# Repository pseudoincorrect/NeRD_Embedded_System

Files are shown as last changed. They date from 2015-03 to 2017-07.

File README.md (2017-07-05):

# Neural activity transmission device 

This repository describe the code of a neural activity transmission device embedded on a rodent.
The purpose of this system is to log the the electrical activity of a rat's neurones onto a computer.

## Global view of the acquisition system 

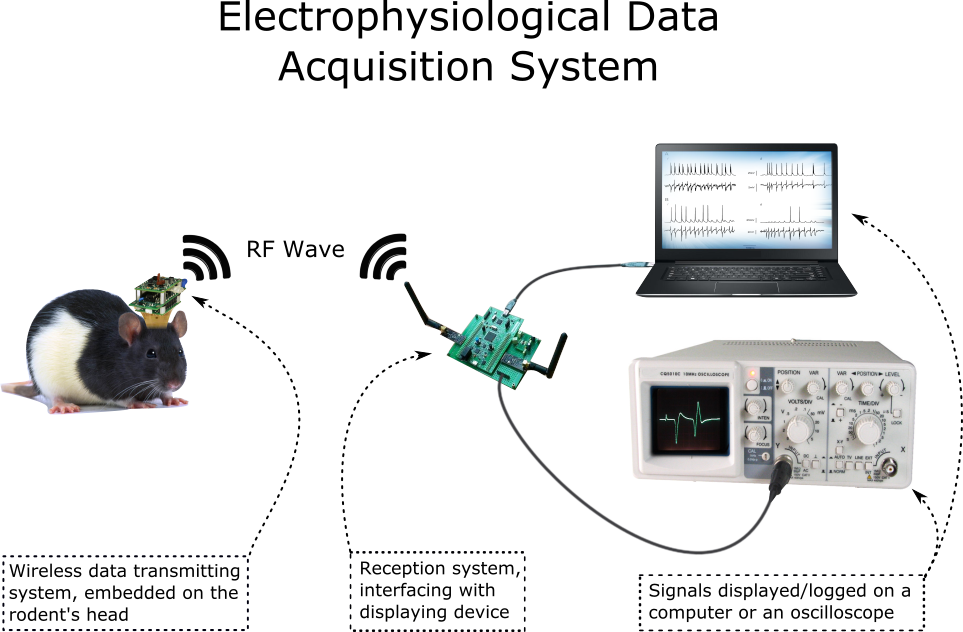
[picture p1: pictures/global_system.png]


[global_system]: https://github.com/pseudoincorrect/Electrophy_Embedded_System/blob/doxygen/pictures/global_system.png?raw=true "Global data acquisition system"

### This repository contain the code and the eagle file necessary to create a the transmitting system embedded on the rodent (see above)

### Features (Embedded Part)

* Omnetics adapter
* Transmit 4 channels of 16 bits at 20 kHz 
* Or 8 channels compressed (16 bits after decompression) at 20 kHz
* Consume 18 mA at 3.7 V at full transmission load
* Weight 7 grams 
* Volume : 2cm *2cm * 2cm 

### Features (Interface Part)

* USB audio protocol interface to display and log on PC
* 8 channels DAC to connect to an acquisition card
* USB as power supply

## Technical part

On this version, we use the Microcontroler [STM32f051C8T7](http://www.st.com/web/en/catalog/mmc/SC1169/SS1574/LN7/PF251889) to interface the Intantech [RHD2132](http://www.intantech.com/products_RHD2000.html) ADC device, and the Nordic Semiconductor [Nrf24l01+](http://www.nordicsemi.com/eng/Products/2.4GHz-RF/nRF24L01) RF transciever.

Eagle files and manual provided in this repertory

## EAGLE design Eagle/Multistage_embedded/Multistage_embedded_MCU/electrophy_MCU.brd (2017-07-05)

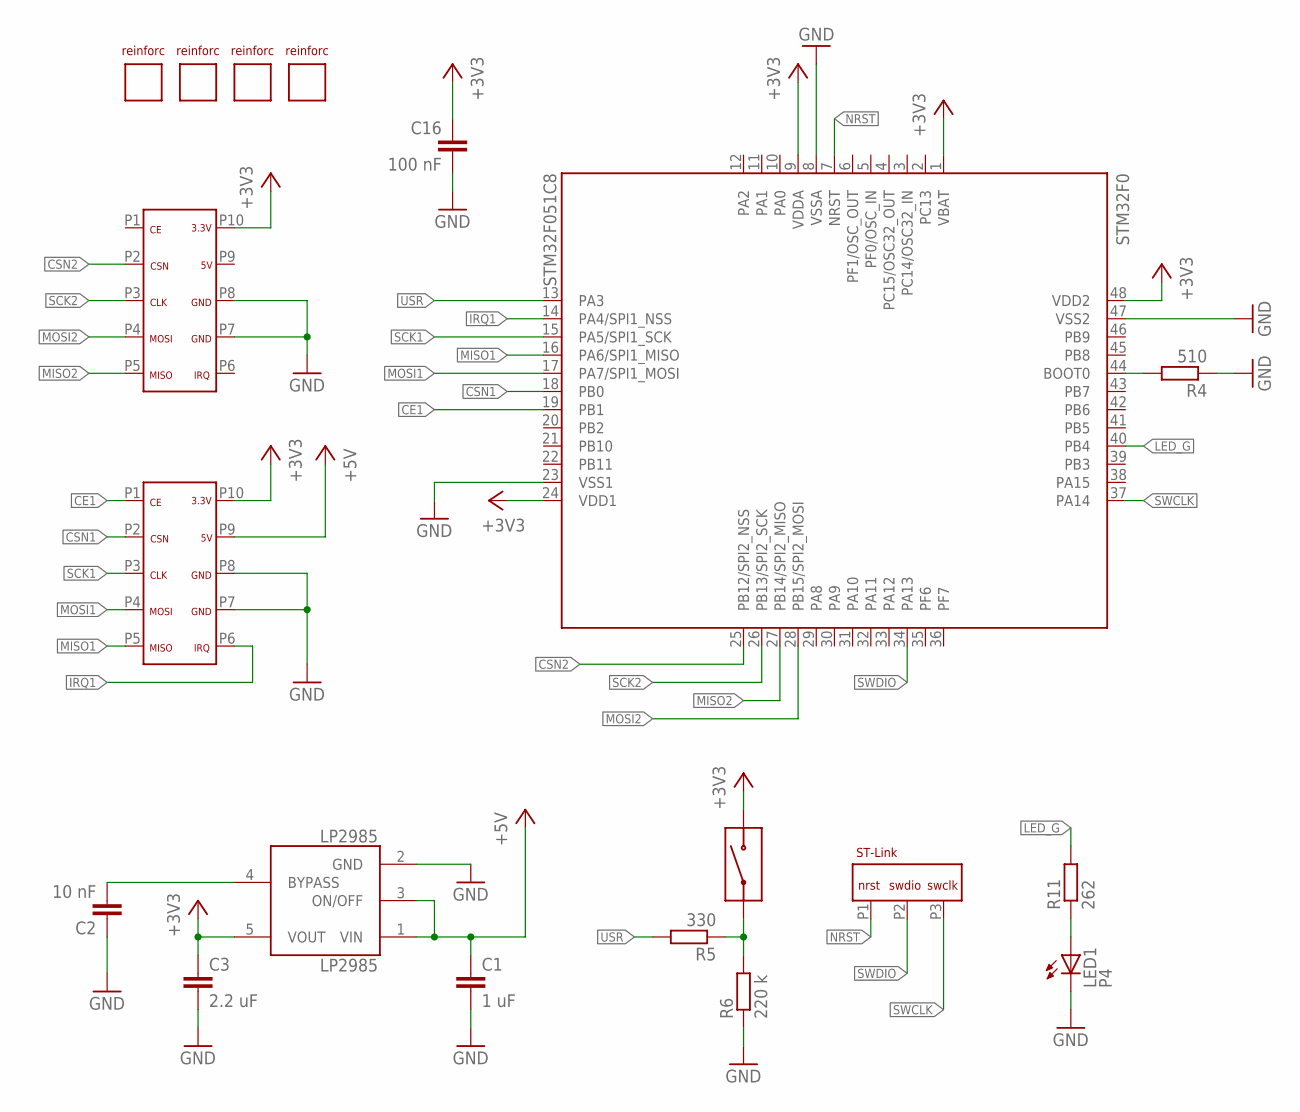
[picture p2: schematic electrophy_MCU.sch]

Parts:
C1: 1 uF; C0603
C2: 10 nF; C0603
C3: 2.2 uF; C0603
C16: 100 nF; C0603
LED1: P4; CHIPLED_0603
LP2985: LP2985AIM5-3.3; SOT25
R4: 510; R0603
R5: 330; R0603
R6: 220 k; R0603
R11: 262; R0603
STM32F0: STM32F051C8; LQFP48-7X7
U$1: DF12-10-FEMALE
U$2: PROGRAM_PIN
U$3: DF12-10-MALE
U$4: TACTILE_BUTTON_THROUGH
U$5, U$6, U$7, U$8: REINFORCEMENT

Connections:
+3V3: C3.1, C16.1, LP2985.5 (VOUT), STM32F0.1 (VBAT), STM32F0.9 (VDDA), STM32F0.24 (VDD1), STM32F0.48 (VDD2), U$1.P10, U$3.P10, U$4.P2 (2)
+5V: C1.1, LP2985.1 (VIN), LP2985.3 (ON/OFF), U$1.P9
BYPASS: C2.2, LP2985.4 (BYPASS)
CE1: STM32F0.19 (PB1), U$1.P1
CSN1: STM32F0.18 (PB0), U$1.P2
CSN2: STM32F0.25 (PB12/SPI2_NSS), U$3.P2
GND: C1.2, C2.1, C3.2, C16.2, LED1.C, LP2985.2 (GND), R4.1, R6.1, STM32F0.8 (VSSA), STM32F0.23 (VSS1), STM32F0.47 (VSS2), U$1.P7, U$1.P8, U$3.P7, U$3.P8
IRQ1: STM32F0.14 (PA4/SPI1_NSS), U$1.P6
LED_G: R11.2, STM32F0.40 (PB4)
MISO1: STM32F0.16 (PA6/SPI1_MISO), U$1.P5
MISO2: STM32F0.27 (PB14/SPI2_MISO), U$3.P5
MOSI1: STM32F0.17 (PA7/SPI1_MOSI), U$1.P4
MOSI2: STM32F0.28 (PB15/SPI2_MOSI), U$3.P4
unnamed: R5.1, R6.2, U$4.P1 (1)
unnamed: R4.2, STM32F0.44 (BOOT0)
unnamed: LED1.A, R11.1
NRST: STM32F0.7 (NRST), U$2.P1
SCK1: STM32F0.15 (PA5/SPI1_SCK), U$1.P3
SCK2: STM32F0.26 (PB13/SPI2_SCK), U$3.P3
SWCLK: STM32F0.37 (PA14), U$2.P3
SWDIO: STM32F0.34 (PA13), U$2.P2
USR: R5.2, STM32F0.13 (PA3)

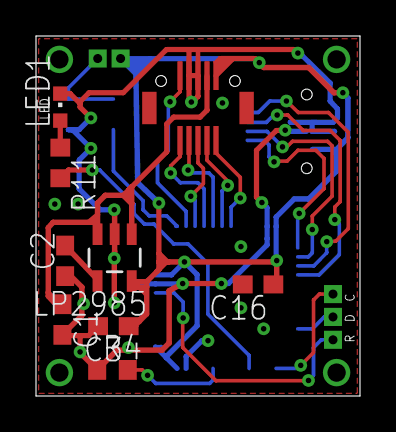
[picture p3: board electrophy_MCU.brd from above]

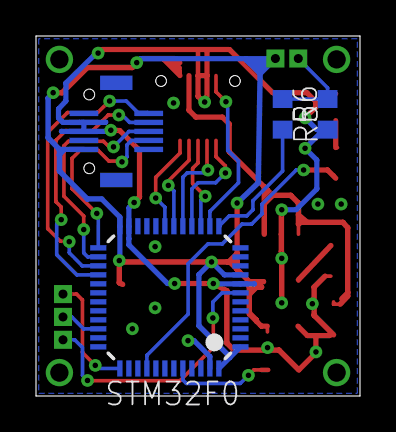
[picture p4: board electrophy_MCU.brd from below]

Board: 2 copper layers, 18.0 x 20.0 mm, 19 parts (5 on the bottom side), 22 nets.

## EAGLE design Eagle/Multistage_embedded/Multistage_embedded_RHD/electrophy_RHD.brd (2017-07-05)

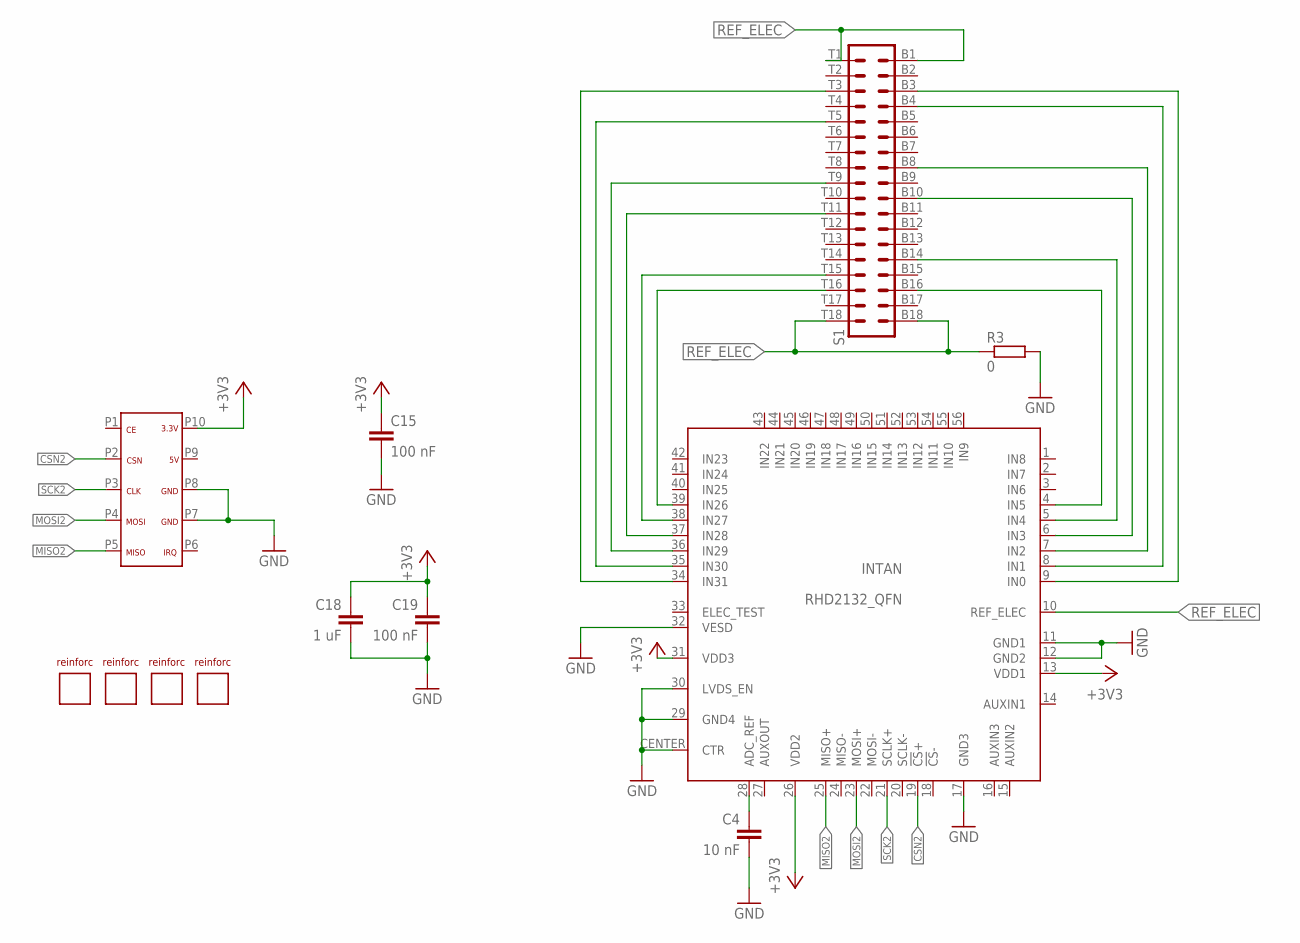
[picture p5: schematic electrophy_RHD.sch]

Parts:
C4: 10 nF; C0603
C15, C19: 100 nF; C0603
C18: 1 uF; C0603
INTAN: RHD2132_QFN; QFN56_8_X_8_LARGE
R3: 0; R0603
S1: OMNETICS_A79027
U$1: DF12-10-FEMALE
U$2, U$3, U$4, U$5: REINFORCEMENT

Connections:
+3V3: C15.1, C18.1, C19.1, INTAN.13 (VDD1), INTAN.26 (VDD2), INTAN.31 (VDD3), U$1.P10
CSN2: INTAN.19 (!CS!+), U$1.P2
GND: C4.2, C15.2, C18.2, C19.2, INTAN.11 (GND1), INTAN.12 (GND2), INTAN.17 (GND3), INTAN.29 (GND4), INTAN.30 (LVDS_EN), INTAN.32 (VESD), INTAN.CENTER (CTR), R3.2, U$1.P7, U$1.P8
MISO2: INTAN.25 (MISO+), U$1.P5
MOSI2: INTAN.23 (MOSI+), U$1.P4
unnamed: INTAN.4 (IN5), S1.B16
unnamed: INTAN.34 (IN31), S1.T3
unnamed: INTAN.35 (IN30), S1.T5
unnamed: INTAN.38 (IN27), S1.T15
unnamed: INTAN.39 (IN26), S1.T16
unnamed: C4.1, INTAN.28 (ADC_REF)
unnamed: INTAN.8 (IN1), S1.B4
unnamed: INTAN.9 (IN0), S1.B3
unnamed: INTAN.5 (IN4), S1.B14
unnamed: INTAN.7 (IN2), S1.B8
unnamed: INTAN.6 (IN3), S1.B10
unnamed: INTAN.36 (IN29), S1.T9
unnamed: INTAN.37 (IN28), S1.T11
REF_ELEC: INTAN.10 (REF_ELEC), R3.1, S1.B1, S1.B18, S1.T1, S1.T18
SCK2: INTAN.21 (SCLK+), U$1.P3

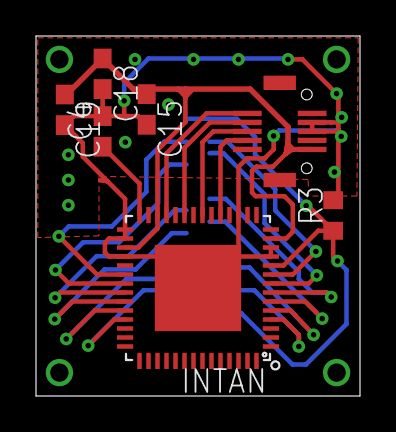
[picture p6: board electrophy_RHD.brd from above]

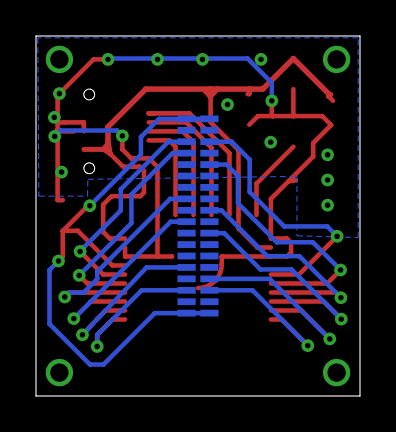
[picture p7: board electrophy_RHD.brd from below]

Board: 2 copper layers, 18.0 x 20.0 mm, 12 parts (2 on the bottom side), 20 nets.

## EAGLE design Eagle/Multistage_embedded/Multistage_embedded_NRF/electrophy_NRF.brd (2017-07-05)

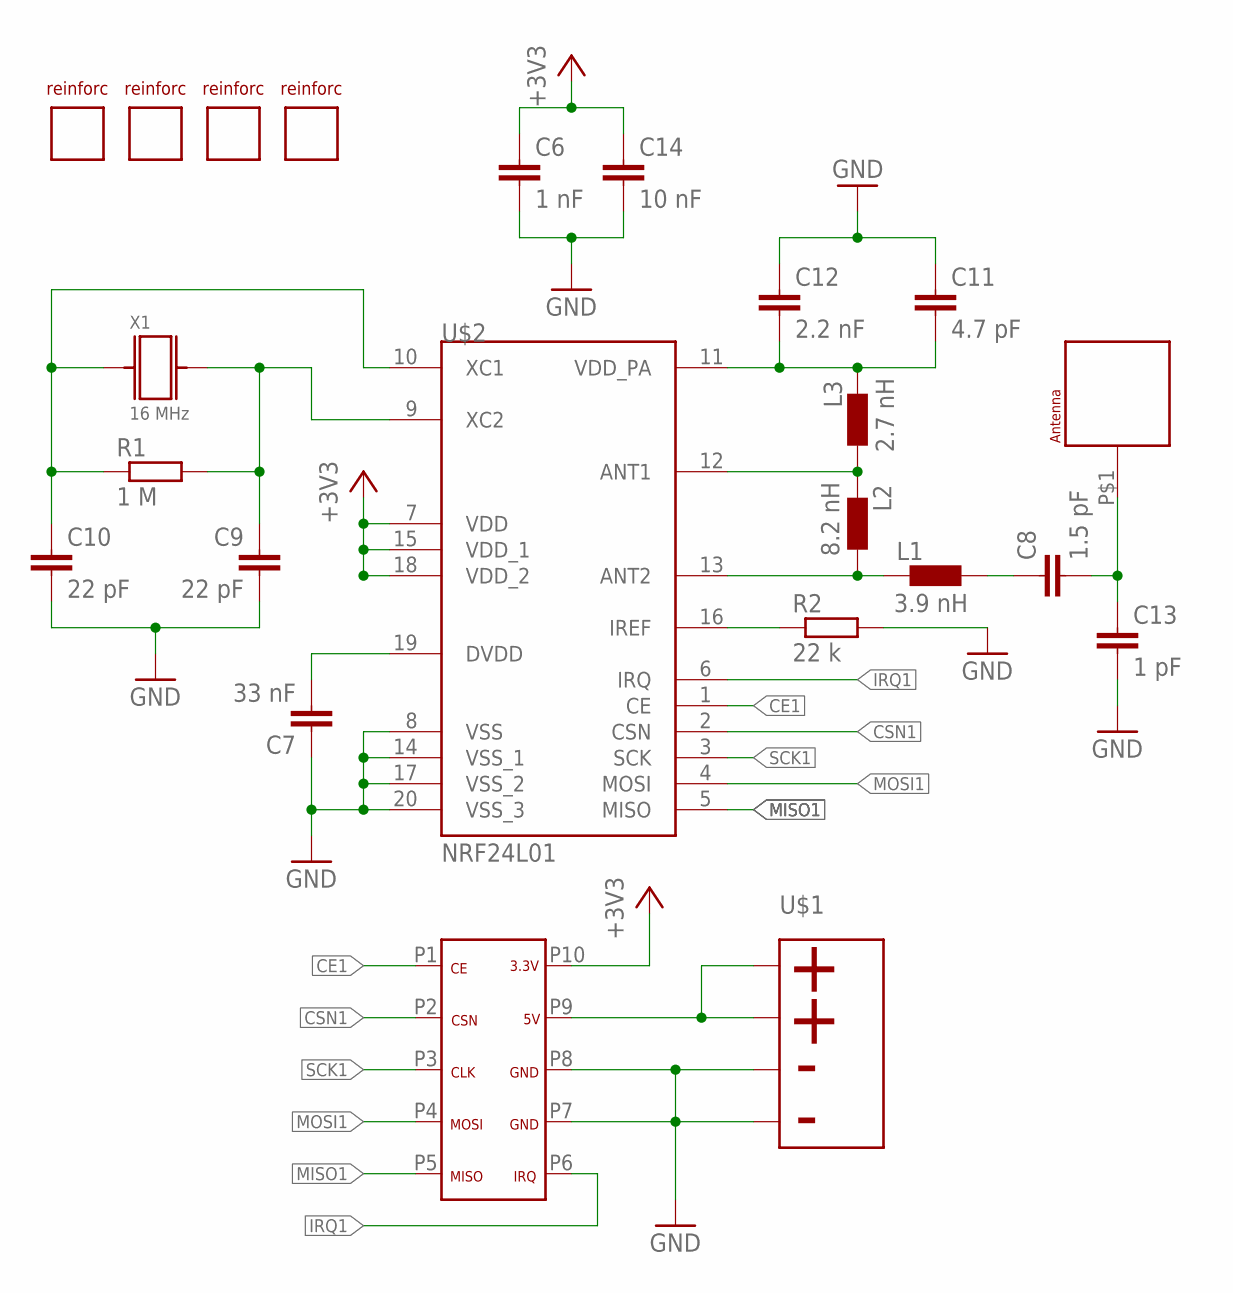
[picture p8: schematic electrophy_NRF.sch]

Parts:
C6: 1 nF; C0603
C7: 33 nF; C0603
C8: 1.5 pF; C0603
C9, C10: 22 pF; C0603
C11: 4.7 pF; C0603
C12: 2.2 nF; C0603
C13: 1 pF; C0603
C14: 10 nF; C0603
L1: 3.9 nH; C0603
L2: 8.2 nH; C0603
L3: 2.7 nH; C0603
R1: 1 M; R0603
R2: 22 k; R0603
U$1: BAT_HOLDER
U$2: NRF24L01; QFN20
U$3: WURTH_ANTENNA
U$4: DF12-10-MALE
U$5, U$6, U$7, U$8: REINFORCEMENT
X1: 16 MHz; NRF_XTAL

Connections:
+3V3: C6.1, C14.1, U$2.7 (VDD), U$2.15 (VDD_1), U$2.18 (VDD_2), U$4.P10
CE1: U$2.1 (CE), U$4.P1
CSN1: U$2.2 (CSN), U$4.P2
GND: C6.2, C7.1, C9.2, C10.2, C11.1, C12.1, C13.2, C14.2, R2.2, U$1.PMOINS, U$1.PMOINSBIS, U$2.8 (VSS), U$2.14 (VSS_1), U$2.17 (VSS_2), U$2.20 (VSS_3), U$4.P7, U$4.P8
IRQ1: U$2.6 (IRQ), U$4.P6
MISO1: U$2.5 (MISO), U$4.P5
MOSI1: U$2.4 (MOSI), U$4.P4
unnamed: C7.2, U$2.19 (DVDD)
unnamed: C11.2, C12.2, L3.2, U$2.11 (VDD_PA)
unnamed: R2.1, U$2.16 (IREF)
unnamed: L1.2, L2.1, U$2.13 (ANT2)
unnamed: C9.1, R1.2, U$2.9 (XC2), X1.P$1 (1)
unnamed: L2.2, L3.1, U$2.12 (ANT1)
unnamed: C8.2, C13.1, U$3.P$1
unnamed: C8.1, L1.1
unnamed: C10.1, R1.1, U$2.10 (XC1), X1.P$2 (2)
PPLUS: U$1.PPLUS, U$1.PPLUSBIS, U$4.P9
SCK1: U$2.3 (SCK), U$4.P3

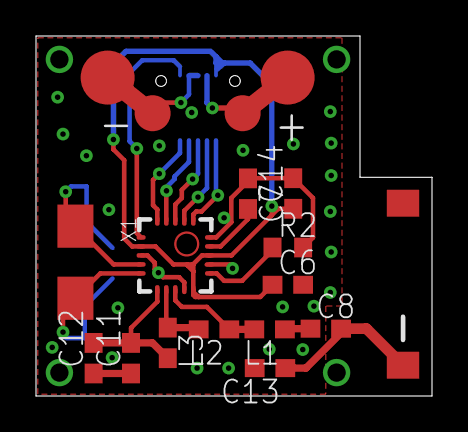
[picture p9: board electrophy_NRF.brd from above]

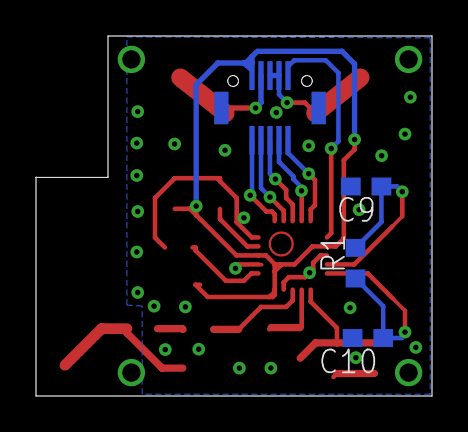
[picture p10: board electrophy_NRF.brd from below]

Board: 2 copper layers, 22.0 x 20.0 mm, 23 parts (4 on the bottom side), 18 nets.

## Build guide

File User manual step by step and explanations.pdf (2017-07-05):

# User manual step by step and explanations

This file will reunite all the instructions to build the hardware part of the rat embedded system and of the interfacing system. We will describe as well how to download the codes in them.

Quick description of the system

The embedded emitting system connected to the implant of the rat, will digitalize the neural signals with an analog to digital converter, compress data, before sending them wirelessly to the second system. This latter, after reception, will decompress data, converted them into USB packets and finally transmit them to the computer for display and recording.

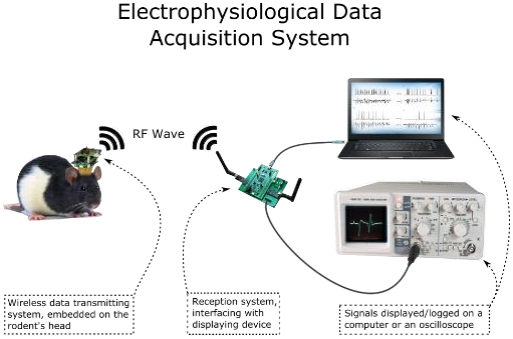
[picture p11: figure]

Summary

I) Building the neural recording System
- How to create, the rat head stage PCB
- Display it on Eagle
- Order it from a PCB creating company on internet
- Solder the components
- How to create the Interfacing system
- Solder components
- How to program the system
- Setup of Keil (software)
- Setup of ST link V2
- Program the two microcontrollers
- How to test the system

II) Explanation about the System • General explanation about the system • Explanations about the Code

Glossary:

MCU: microcontroller
RHD: Rhd2132 the analog to digital module that will convert the neural signal of the rat
NRF: | Nrf24L01+ the transceiver module used to communicate wirelessly
PCB: | Printed circuit board
Embedded system: | the system that will be carried by the rat on its head
Interfacing system: | the system that will do the interface between the embedded system and the
computer

# Building the neural recording System

# How to create, the rat head stage PCB

## Display on Eagle

First, we have to download Eagle, a software from Cadsoft from their website. The free version, is enough. We take the last version, corresponding with our OS (windows 7, 64 bits in our case)

http://www.cadsoftusa.com/download-eagle

Now, it’s time to install it.

Now download the file: [lien]
Since the Embedded system is composed of 3 sub-systems, we have 3 different eagle files/folders. We open one of the, for instance [blab la bla.egl].

We can follow this [link tutorial] tutorial to increase our understanding and be able to navigate between files. As we open it, three windows will be displayed one for the project manager, one for the schematics of the circuit and one for the actual representation and design of the circuit.

Order PCB’s

Since we only want to order printed circuit and not design it, we won’t say more about eagle. Many tutorial are available on internet.

To order the printed circuits, we need to pick on PCB manufacturer available on internet and which accept PCB layout file under eagle file format. For the following of this tutorial, we will use PCB-Pool printed circuit manufacturer: [pcb pool]

Again, since the embedded system is composed of 3 PCB, we have to do 3 orders. On the PCB pol website (the English version), we go to “Order” → “PCB’s”. Then we fill the formulary. To reduce the price you can unselect some option, but we advise to use the option as shown below. Also you can select another manufacturer to reduce the costs. The solution we give is just a working example.

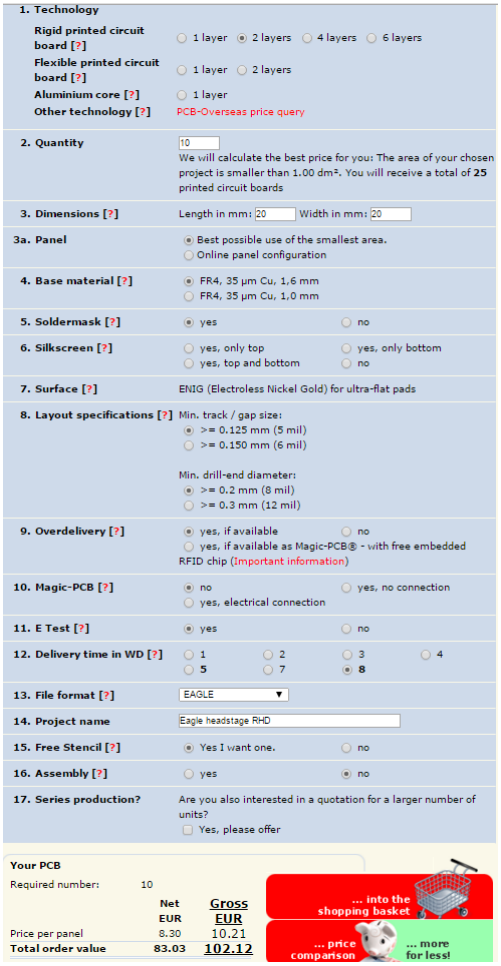
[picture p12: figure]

Components list
Be sure to order every components needed, which are listed [here] in their correct package.

## Soldering

Soldering is the most delicate part of building the system. Many technics are usable such as using a soldering iron, a hot air soldering station, or a reflow oven. In our case we soldered every component except the RHD2132 and the NRF24L01+ whit a soldering iron. For the later component, we used a hot air soldering station. About soldering, many tutorials exists as well (youtube.com).
The advices we can give are the following:
- Use a microscope or a good lens
- Set first the components intended to be soldered by hot air
- Then set first the most complicated to solder components (microcontroller, Led, connectors)

How to create the interface system

The interface system is centered on a STMicroelectronics development board, the STM32F411 development board:

http://www.st.com/web/catalog/tools/FM116/SC959/SS1532/LN1848/PF260946

Follow this list of components to create the interfacing system

[List]

And solder them following that schematic.

[Schematic]
There is no particular difficulties for soldering these components.

# How to program the system

This section will speak about how to set up the system. We won’t approach the understanding of the code and the utilization of Keil the development tool used to develop the code and debug the system. We will see how to compile the code and program both MCU’s.

First we need to install the last version of Keil:
- Let’s go to: http://www.keil.com/
- Then: “product download” → “MDK-ARM”
- Then: we complete the formulary and download the software compatible with our Operating system, in our case, windows 7, and 64 bits.
- Then we install it.

- Doing this quick tutorial will help you a lot about working with Keil and the microcontroller we want to program:
http://www.keil.com/appnotes/files/apnt_261.pdf

Now it’s time to download the code from internet, open it in Keil and compile it.
Since we have two systems: the rat embedded one and the interfacing one, there is two projects under Keil. One project to create the code for each microcontroller. We want to compile the code of each project one at time, compile it, and download it to the corresponding microcontroller.

For that:
We go to: https://github.com/pseudoincorrect/Electrophy_Base_System
And click on “download zip”.

Then we go to: https://github.com/pseudoincorrect/Electrophy_Embedded_System And click on “download zip” as well.

## Keil project setting up

On each folder (after unzipping), we navigate to: Base_System or Embedded_System → Projects → MDK-ARM → and open the .uvprojx file (either Embedded_System.uvprojx or Base_System.uvprojx)

This will open the corresponding Keil project. Since we presume it’s the first we open Keil, some packages are needed to be added in order to compile properly and to download the code to the MCU.

After open, Keil will ask to choose either:
“Migrate to Device Pack” or “Install Legacy Support”, we choose the first one, “Migrate to Device Pack”.

Then depending which project we opened we will follow the appropriate one

## For the INTERFACING SYSTEM

If the “pack installer” is not opened, we open it by clicking on “Project” →“Manage” →“Pack installer”

Base_System.uvprojx

Go to device TAB
Go to:
“STMincroelectronics” →
“STM32F4 Series” | →
“STM32F411VE” | →
Click on “STM32F411VETx”

Go to Packs TAB
Install:
“Keil::STM32F4xx_DFP”

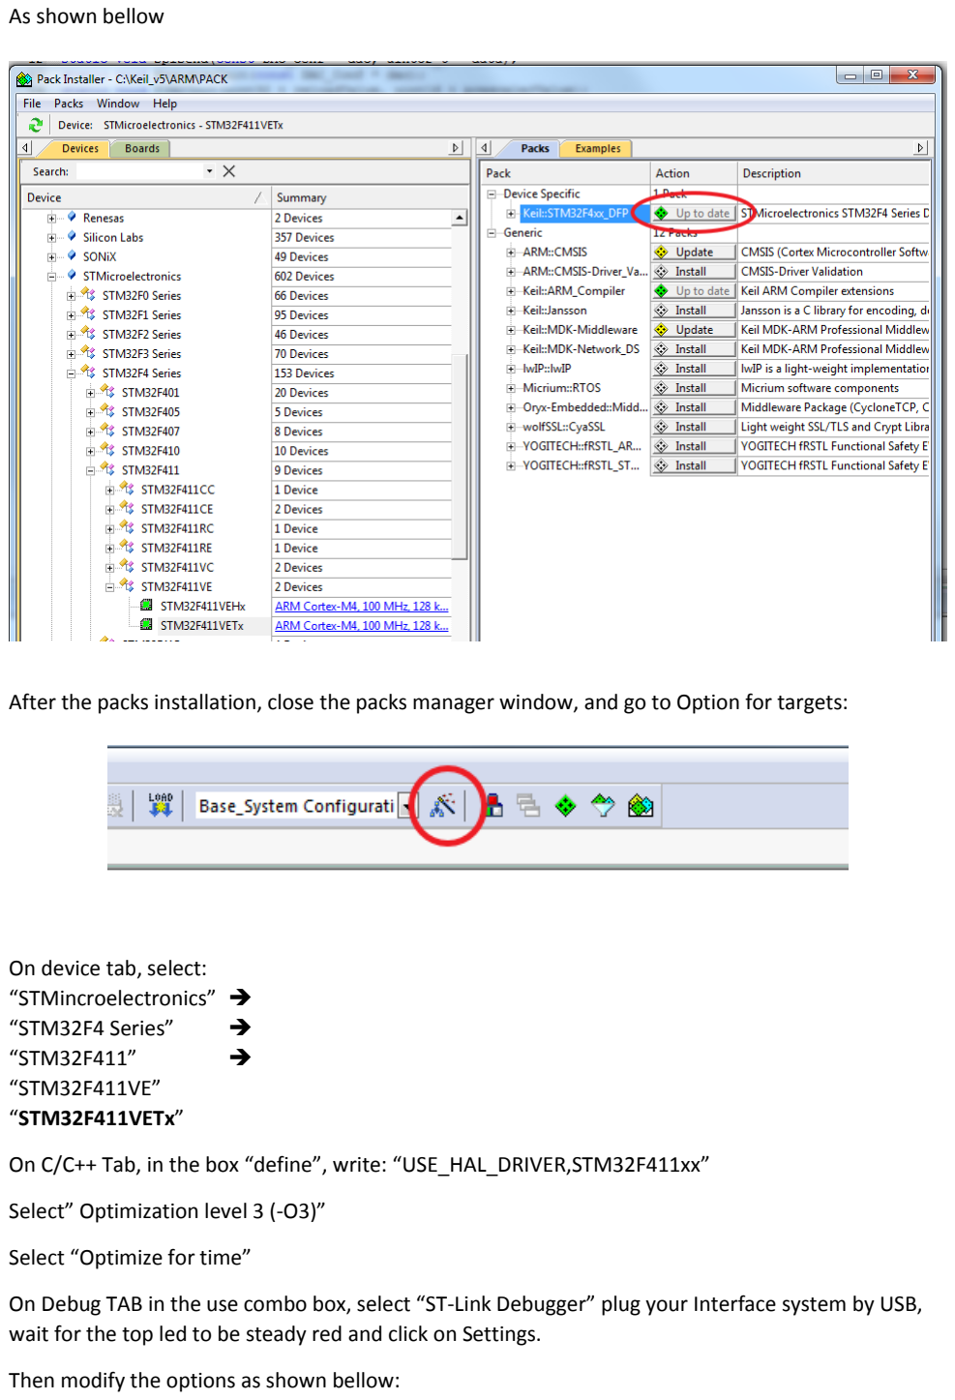
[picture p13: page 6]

As shown bellow

After the packs installation, close the packs manager window, and go to Option for targets:

On device tab, select:
“STMincroelectronics” →
“STM32F4 Series” | →
“STM32F411” | →
“STM32F411VE”
“STM32F411VETx”

On C/C++ Tab, in the box “define”, write: “USE_HAL_DRIVER,STM32F411xx”

Select” Optimization level 3 (-O3)”

Select “Optimize for time”

On Debug TAB in the use combo box, select “ST-Link Debugger” plug your Interface system by USB, wait for the top led to be steady red and click on Settings.

Then modify the options as shown bellow:

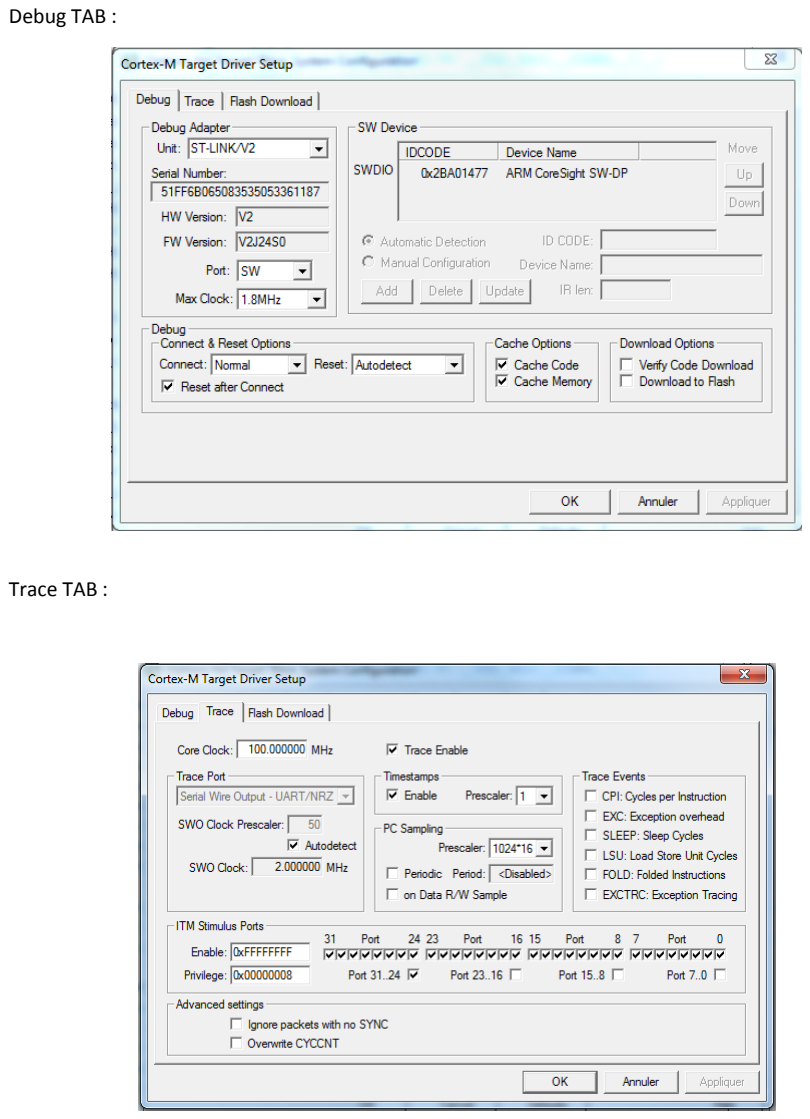
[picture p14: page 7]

Debug TAB :

Trace TAB :

Flash Download TAB:

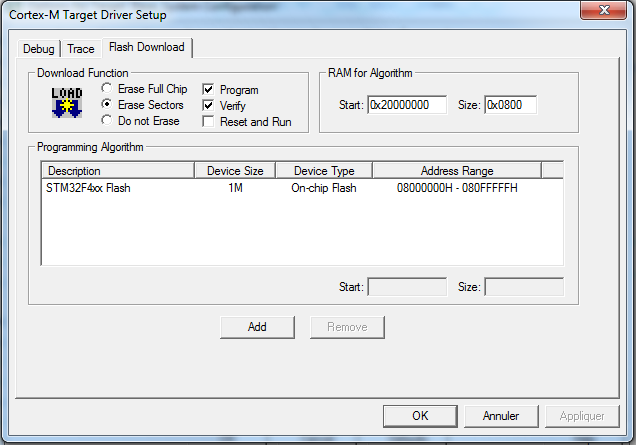
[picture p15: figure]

If there is nothing in Program Algorithm, select the one above “STM324xx Flash” by clicking on “Add”.

If this algorithm isn’t proposed, it’s because the proper pack isn’t installed, in pack manager, as saw above.

## For the EMBEDDED SYSTEM

If the “pack installer” is not opened, we open it by clicking on “Project” →“Manage” →“Pack installer”

Base_System.uvprojx

Go to device TAB
Go to:
“STMincroelectronics” →
“STM32F0 Series” | →
“STM32F051” | →
Click on “STM32F051C8”

Go to Packs TAB
Install:
“Keil::STM32F0xx_DFP”

As shown bellow

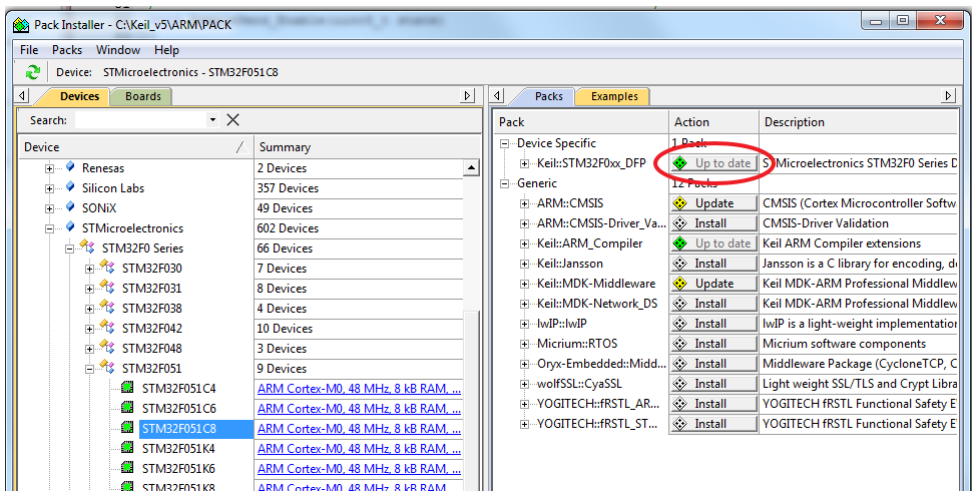
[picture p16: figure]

After the packs installation, close the packs manager window, and go to Option for targets:

On device tab, select:
“STMincroelectronics” →
“STM32F0 Series” | →
“STM32F051” | →
“STM32F051C8”

On C/C++ Tab, in the box “define”, write: “USE_HAL_DRIVER,STM32F051x8”

Select” Optimization level 3 (-O3)”

Select “Optimize for time”

On Debug TAB in the use combo box, select “ST-Link Debugger” plug your Interface system by USB, wait for the top led to be steady red and click on Settings.

Then modify the options as shown below

Debug TAB:

Trace TAB:

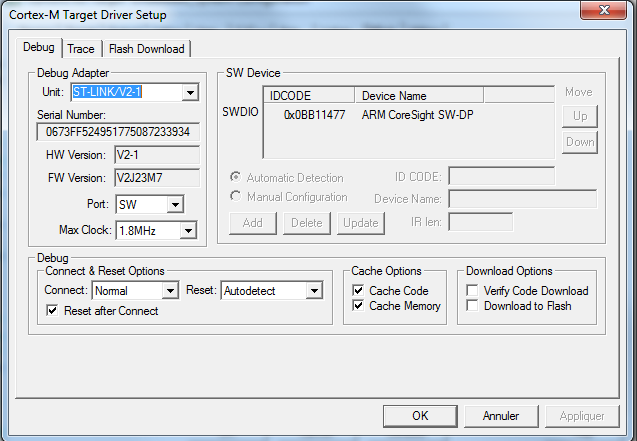
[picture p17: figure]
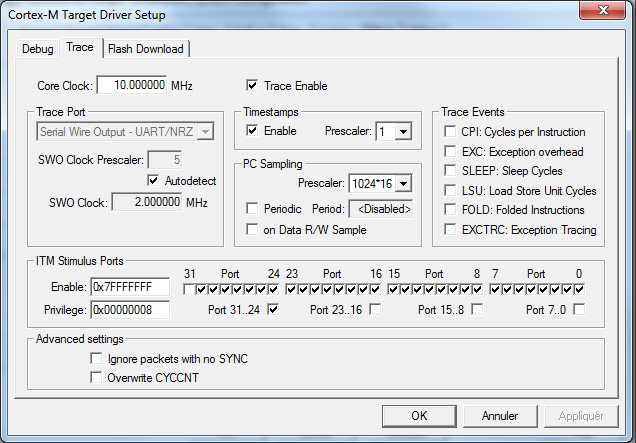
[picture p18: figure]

Flash Download TAB:

If there is nothing in Program Algorithm, select the one above “STM324xx Flash” by clicking on “Add”.

If this algorithm isn’t proposed, it’s because the proper pack isn’t installed, in pack manager, as saw above.

## Compilation of the Code and download to the microcontroller

To compile the code click on the Rebuild icon

If the compilation succeeded, we will get this message in the build Output console:

Otherwise, if we get error, a “Target not created” message will be displayed in the console. Which in that case a debugging is needed.

Now that the compilation was successful, we check that the target (the microcontroller) is linked and detected by the software by clicking on “option for target” → “Debug” tab → “Settings” button. And see if there is “ARM CoreSight SW-DP” in the SW Device block.

Then close the windows and click on “Download”

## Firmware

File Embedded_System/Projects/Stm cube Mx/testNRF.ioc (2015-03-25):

#MicroXplorer Configuration settings - do not modify
#Wed Jan 28 12:24:36 CET 2015
Dma.Request0=SPI1_TX
Dma.RequestsNb=1
Dma.SPI1_TX.0.Direction=DMA_MEMORY_TO_PERIPH
Dma.SPI1_TX.0.Instance=DMA1_Channel3
Dma.SPI1_TX.0.MemDataAlignment=DMA_MDATAALIGN_BYTE
Dma.SPI1_TX.0.MemInc=DMA_MINC_ENABLE
Dma.SPI1_TX.0.Mode=DMA_NORMAL
Dma.SPI1_TX.0.PeriphDataAlignment=DMA_PDATAALIGN_BYTE
Dma.SPI1_TX.0.PeriphInc=DMA_PINC_DISABLE
Dma.SPI1_TX.0.Priority=DMA_PRIORITY_LOW
Dma.SPI1_TX.0.RequestParameters=Instance,Direction,PeriphInc,MemInc,PeriphDataAlignment,MemDataAlignment,Mode,Priority
File.Version=4
KeepUserPlacement=false
Mcu.Family=STM32F0
Mcu.IP0=DMA
Mcu.IP1=NVIC
Mcu.IP2=RCC
Mcu.IP3=SPI1
Mcu.IP4=SPI2
Mcu.IPNb=5
Mcu.Name=STM32F051C8Tx
Mcu.Package=LQFP48
Mcu.Pin0=PA4
Mcu.Pin1=PA5
Mcu.Pin10=PA15
Mcu.Pin11=PB4
Mcu.Pin12=PB5
Mcu.Pin2=PA6
Mcu.Pin3=PA7
Mcu.Pin4=PB0
Mcu.Pin5=PB1
Mcu.Pin6=PB13
Mcu.Pin7=PB14
Mcu.Pin8=PB15
Mcu.Pin9=PF7
Mcu.PinsNb=13
Mcu.UserName=STM32F051C8Tx
MxCube.Version=4.5.0
NVIC.DMA1_Channel2_3_IRQn=true\:0\:0\:false
NVIC.SPI2_IRQn=true\:0\:0\:false
NVIC.SysTick_IRQn=true\:0\:0\:false
PA15.Locked=true
PA15.Signal=GPIO_Input
PA4.GPIOParameters=GPIO_PuPd,GPIO_Label,GPIO_Mode
PA4.GPIO_Label=Spi1Nss
PA4.GPIO_Mode=GPIO_MODE_INPUT
PA4.GPIO_PuPd=GPIO_NOPULL
PA4.Locked=true
PA4.Signal=GPIO_Input
PA5.Mode=Full_Duplex_Master
PA5.Signal=SPI1_SCK
PA6.Mode=Full_Duplex_Master
PA6.Signal=SPI1_MISO
PA7.Mode=Full_Duplex_Master
PA7.Signal=SPI1_MOSI
PB0.Locked=true
PB0.Signal=GPIO_Output
PB1.Locked=true
PB1.Signal=GPIO_Output
PB13.Mode=Full_Duplex_Master
PB13.Signal=SPI2_SCK
PB14.Mode=Full_Duplex_Master
PB14.Signal=SPI2_MISO
PB15.Mode=Full_Duplex_Master
PB15.Signal=SPI2_MOSI
PB4.Locked=true
PB4.Signal=GPIO_Output
PB5.Locked=true
PB5.Signal=GPIO_Output
PCC.Family=STM32F0
PCC.MCU=STM32F051C8Tx
PCC.MXVersion=4.5.0
PCC.PartNumber=STM32F051C8Tx
PCC.Seq0=0
PCC.SubFamily=STM32F0x1
PCC.Temperature=25
PCC.Vdd=3.6
PF7.Locked=true
PF7.Signal=GPIO_Output
ProjectManager.AskForMigrate=true
ProjectManager.BackupPrevious=false
ProjectManager.CompilerOptimize=2
ProjectManager.ComputerToolchain=false
ProjectManager.CoupleFile=false
ProjectManager.DeletePrevious=true
ProjectManager.DeviceId=STM32F051C8Tx
ProjectManager.FirmwarePackage=STM32Cube FW_F0 V1.1.0
ProjectManager.FreePins=false
ProjectManager.HalAssertFull=false
ProjectManager.KeepUserCode=true
ProjectManager.LastFirmware=true
ProjectManager.LibraryCopy=0
ProjectManager.ProjectBuild=false
ProjectManager.ProjectFileName=Embedded_System.ioc
ProjectManager.ProjectName=Embedded_System
ProjectManager.TargetToolchain=MDK-ARM 4.73
RCC.AHBFreq_Value=48000000
RCC.APB1Freq_Value=48000000
RCC.APB1TimFreq_Value=48000000
RCC.CECFreq_Value=32786.88524590164
RCC.FCLKCortexFreq_Value=48000000
RCC.FamilyName=M
RCC.HCLKFreq_Value=48000000
RCC.HSICECFreq_Value=32786.88524590164
RCC.I2SFreq_Value=48000000
RCC.IPParameters=PLLMUL,FamilyName,PLLMCOFreq_Value,APB1TimFreq_Value,HCLKFreq_Value,I2SFreq_Value,FCLKCortexFreq_Value,HSICECFreq_Value,CECFreq_Value,AHBFreq_Value,TimSysFreq_Value,USART1Freq_Value,SYSCLKFreq_VALUE,SYSCLKSource,MCOFreq_Value,APB1Freq_Value,PLLCLKFreq_Value
RCC.MCOFreq_Value=48000000
RCC.PLLCLKFreq_Value=48000000
RCC.PLLMCOFreq_Value=24000000
RCC.PLLMUL=RCC_PLL_MUL12
RCC.SYSCLKFreq_VALUE=48000000
RCC.SYSCLKSource=RCC_SYSCLKSOURCE_PLLCLK
RCC.TimSysFreq_Value=6000000
RCC.USART1Freq_Value=48000000
SPI1.BaudRatePrescaler-Full_Duplex_Master=SPI_BAUDRATEPRESCALER_4
SPI1.CalculateBaudRate-Full_Duplex_Master=12.0 MBits/s
SPI1.DataSize-Full_Duplex_Master=SPI_DATASIZE_8BIT
SPI1.IPParameters=Mode-Full_Duplex_Master,BaudRatePrescaler-Full_Duplex_Master,CalculateBaudRate-Full_Duplex_Master,DataSize-Full_Duplex_Master
SPI1.Mode-Full_Duplex_Master=SPI_MODE_MASTER
SPI2.BaudRatePrescaler-Full_Duplex_Master=SPI_BAUDRATEPRESCALER_4
SPI2.CalculateBaudRate-Full_Duplex_Master=12.0 MBits/s
SPI2.DataSize-Full_Duplex_Master=SPI_DATASIZE_16BIT
SPI2.IPParameters=Mode-Full_Duplex_Master,BaudRatePrescaler-Full_Duplex_Master,CalculateBaudRate-Full_Duplex_Master,DataSize-Full_Duplex_Master
SPI2.Mode-Full_Duplex_Master=SPI_MODE_MASTER

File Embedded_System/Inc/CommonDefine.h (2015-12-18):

#ifndef __COMMONDEFINE_H__
#define __COMMONDEFINE_H__

/********************************************************************/
//CHANGEABLE PARAMETER 

// This mode will generate an artifiacial signal (a sort of replacement of te RHD acquired signal) to test the system
//#define TESTBUFFER

//enable the change of Eta and Beta via receiver inputs
//#define PARAMETER_SELECTION 

// On compressing mode, compress only 4 chanel and send at the same time their non-compressed value to compare
#define COMPARISON 

#define ETA_      512					    // adaptation parameter
#define BETA_     8					     // error parameter
#define H_        120/128


/********************************************************************/
// FIXED PARAMETERS 
#define LOW		0
#define HIGH	1

#define CHANNEL_SIZE 	0x08 // must be a multiple of BYTES_PER_FRAME (NRF.h)

#define BYTES_PER_FRAME	   32 // ammount of byte in one packet transmission
#define NUMBER_OF_PACKETS	 30 // number of packet send at once (size of the buffer)
#define SAMPLE_BUFFER_SIZE 	(BYTES_PER_FRAME * NUMBER_OF_PACKETS) // defined in NRF.h

#define SIZE_BUFFER_RHD		 70	
#define SIZE_BUFFER_NRF		 3

#define NBIT 	2		// resolution of the compression

#define POW_2_NBIT  	(1 << NBIT) 			// 2^NBIT
#define CUT_VAL_SIZE 	(POW_2_NBIT - 1) // number of cut value


#define DEBUG_HIGH 	(GPIOA->BSRR |= GPIO_PIN_3)
#define DEBUG_LOW		(GPIOA->BSRR |= ((uint32_t) GPIO_PIN_3 << 16))

#define	SIZE_VALUE	 	 	25
#define INTERVAL_TEST  	4
#define SIZE_TEST				(SIZE_VALUE * INTERVAL_TEST)

#define STATE_INIT			__8ch_2bit__20kHz__C__

/**************************************************************/
//					Enum
/**************************************************************/
typedef enum
{
	__8ch_2bit__20kHz__C__ = 0x01,
	__4ch_16bit_20kHz_NC__ = 0x02,
	__8ch_16bit_10kHz_NC__ = 0x03,
  __8ch_8bit__20kHz_NC__ = 0x04,
  
} DataStateTypeDef;

#endif

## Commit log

2015-06-20 Leds Ok , fbar to improve, rhd chanel selction and DAC to test
2017-07-05 add supportive file
    add supportive file
    manual
    eagle file
    [electrophy_MCU.brd, electrophy_MCU.sch, electrophy_NRF.brd, electrophy_NRF.sch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]
